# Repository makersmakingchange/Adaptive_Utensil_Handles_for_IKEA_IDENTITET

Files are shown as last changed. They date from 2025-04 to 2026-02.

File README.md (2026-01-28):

<!--- Open Source Assistive Technology: GitHub Readme Template Version 1.2 (2024-May-27)  --->

<!--- TITLE --->
# Adaptive Utensil Handles for IKEA IDENTITET

> [!IMPORTANT]
2026-Jan-28 The cutlery set is currently unavailable from IKEA Canada.

## Overview
<!--- A brief summary of the project. What it does, who it is for, how much it costs. --->
The Adaptive Utensil Handles for IKEA® IDENTITET™ is an assistive technology device that provides a cost-effective way for individuals who struggle to grasp and manipulate utensils to eat independently.

The handles are comprised of 3D printed parts that encapsulate the fork and/or spoon from the [commercially available IKEA® IDENTITET™ cutlery set](https://www.ikea.com/ca/en/p/identitet-16-piece-cutlery-set-stainless-steel-50578174/) . 

The Adaptive Utensil Handles are an open assistive technology (OpenAT). Under the terms of the open source licenses, the device may be built, used, and improved upon by anyone.

The overall cost of materials for a set of utensils and full set of handles is about $20 CAD.  

*IKEA® and IDENTITET™ are trademarks of Inter IKEA Systems B.V. This device is not affiliated with, endorsed by, or sponsored by IKEA.*

An IKEA Identitet fork in an adapted handle, along with several other handle variants.

## Makers Making Change Assistive Device Library
https://www.makersmakingchange.com/s/product/adaptive-utensil-handles-for-ikea-identitet/01tJR000008gxv7YAA 

## How to Obtain the Device
### 1. Do-it-Yourself (DIY) or Do-it-Together (DIT)

This is an open-source assistive technology, so anyone is free to build it. All of the files and instructions required to build the device are contained within this repository. Refer to the Maker Guide below.

### 2. Request a build of this device

You may also submit a build request through the [Makers Making Change Assistive Device Library Listing](https://www.makersmakingchange.com/s/product/adaptive-utensil-handles-for-ikea-identitet/01tJR000008gxv7YAA) to have a volunteer maker build the device. As the requestor, you are responsible for reimbursing the maker for the cost of materials and any shipping.

### 3. Build this device for someone else

If you have the skills and equipment to build this device, and would like to donate your time to create the device for someone who needs it, visit the [MMC Maker Wanted](https://makersmakingchange.com/maker-wanted/) section.

## Build Instructions
<!--- Outline the major steps required to create a build --->

### 1. Read through the Maker Guide

The [Maker Guide](/Documentation/Adaptive_Utensils_Maker_Guide.pdf)  contains all the necessary information to build this device, including tool lists, assembly instructions, programming instructions (if applicable) and testing.

### 2. Order the Off-The-Shelf Components

The [Bill of Materials](/Documentation/Adaptive_Utensils_BOM.xlsx) lists all of the parts and components required to build the device.

### 3. Print the 3D Printable components

All of the files and individual print files can be found in the [/Build_Files/3D_Printing_Files](/Build_Files/3D_Printing_Files/) folder.

### 4. Assemble the <DeviceName>

Reference the Assembly Guide section of the [Maker Guide](/Documentation/Adaptive_Utensils_Maker_Guide.pdf) for the tools and steps required to build the device.

## How to improve this Device
As open source assistive technology, you are welcomed and encouraged to improve upon the design. 

## Files
### Documentation
<!--- Update the name, link, and version for documentation --->
| Document             | Version | Link |
|----------------------|---------|------|
| Design Workbook     | 1.0     | [Adaptive_Utensils_Design_Workbook](/Documentation/Adaptive_Utensils_Design_Workbook.pdf)     |
| Design Rationale     | 1.0     | [Adaptive_Utensils_Design_Rationale](/Documentation/Adaptive_Utensils_Design_Rationale.pdf)     |
| Maker Guide          | 1.0     | [Adaptive_Utensils_Maker_Guide](/Documentation/Adaptive_Utensils_Maker_Guide.pdf)     |
| Bill of Materials    | 1.0     | [Adaptive_Utensils_Bill_of_Materials](/Documentation/Adaptive_Utensils_BOM.xlsx)     |
| User Guide           | 1.0     | [Adaptive_Utensils_User_Guide](/Documentation/Adaptive_Utensils_User_Guide.pdf)    |
| Changelog            | 1.0     | [Changelog](CHANGES.txt)     |

### Design Files
<!--- Include a copy of the original design files to facilitate easy editing and customization. Consider also including a generic format (e.g., STEP) --->
 - [CAD Files](/Design_Files/CAD_Design_Files)
 - [PCB Files](/Design_Files/PCB_Design_Files)

### Build Files
<!--- Include a copy of the build files intended for manufacturing. This may include svg files for laser cutting, stl files for 3d printing, Gerber files for custom PCBs, and Arduino files for custom firmware. --->
 - [3D Printing Files](/Build_Files/3D_Printing_Files)

## License
<!--- Add the year(s) for the copyright and the Designer Name. You may use the standard set of open licenses or choose your own for the hardware, software, and accompanying materials. --->
Copyright (C) 2024-2025, Alberta Health Services, Research and Innovation.

This work is licensed under a Creative Commons Attribution Non-commercial-Share Alike 4.0 International license. To view a copy of this licence, see https://creativecommons.org/licenses/by-nc-sa/4.0/. You are free to copy, distribute and adapt the work for non-commercial purposes, as long as you attribute the work to Alberta Health Services and abide by the other licence terms. If you alter, transform, or build upon this work, you may distribute the resulting work only under the same, similar, or compatible licence. The licence does not apply to AHS trademarks, logos or content for which Alberta Health Services is not the copyright 
owner.

This material is intended for general information only and is provided on an "as is", "where is" basis. Although reasonable efforts were made to confirm the accuracy of the information, Alberta Health Services does not make any representation or warranty, express, implied or statutory, as to the accuracy, reliability, completeness, applicability or fitness for a particular purpose of such information. This material is not a substitute for the advice of a qualified health professional. Alberta Health Services expressly disclaims all liability for the use of these materials, and for any claims, actions, demands or suits arising from such use.

## Attribution
<!--- Provide any necessary attribution for designs or components that are included in the device or as part of the project. --->
The device was designed and documented by Alberta Health Services, Research and Innovation. 

<!--- This is the attribution for the template. --->
The documentation template was created by Makers Making Change / Neil Squire Society and is used under a CC BY-SA 4.0 license. It is available at the following link: [https://github.com/makersmakingchange/OpenAT-Template](https://github.com/makersmakingchange/OpenAT-Template)

### Contributors
<!--- List the names of the people that contributed to the design. This could include the original source of the idea, designers, testers, documenters, etc. --->
 - Anson Chung 
 - Kendra Smart 
 - Holden Holzer
 - Tod Vandenberg
 - Michael Cimolini
 - Adam Bulat
 - Robert Hirsche

----

<!-- ABOUT MMC START -->
## About Makers Making Change
[Makers Making Change Logo](https://www.makersmakingchange.com/)

Makers Making Change is a program of [Neil Squire](https://www.neilsquire.ca/), a Canadian non-profit that uses technology, knowledge, and passion to empower people with disabilities.

Makers Making Change leverages the capacity of community based Makers, Disability Professionals and Volunteers to develop and deliver affordable Open Source Assistive Technologies.

 - Website: [www.MakersMakingChange.com](https://www.makersmakingchange.com/)
 - GitHub: [makersmakingchange](https://github.com/makersmakingchange)
 - Bluesky: [@makersmakingchange.bsky.social](https://bsky.app/profile/makersmakingchange.bsky.social)
 - Instagram: [@makersmakingchange](https://www.instagram.com/makersmakingchange)
 - Facebook: [makersmakechange](https://www.facebook.com/makersmakechange)
 - LinkedIn: [Neil Squire Society](https://www.linkedin.com/company/neil-squire-society/)
 - Thingiverse: [makersmakingchange](https://www.thingiverse.com/makersmakingchange/about)
 - Printables: [MakersMakingChange](https://www.printables.com/@MakersMakingChange)

### Contact Us
For technical questions, to get involved, or to share your experience we encourage you to [visit our website](https://www.makersmakingchange.com/) or [contact us](https://www.makersmakingchange.com/s/contact).
<!-- ABOUT MMC END -->

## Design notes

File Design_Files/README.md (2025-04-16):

<!--- Open Source Assistive Technology Template: GitHub Design Files Readme Version 1.2 (2025-Feb-04)  --->

This folder contains the design files for the device.

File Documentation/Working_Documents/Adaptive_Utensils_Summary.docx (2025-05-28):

# Overview

The Device Summary is intended to be a detailed summary of the device, product, and maker information for the Adaptive Utensils, making it easier to add to the Makers Making Change website. It is intended for anyone who will view the device listing.

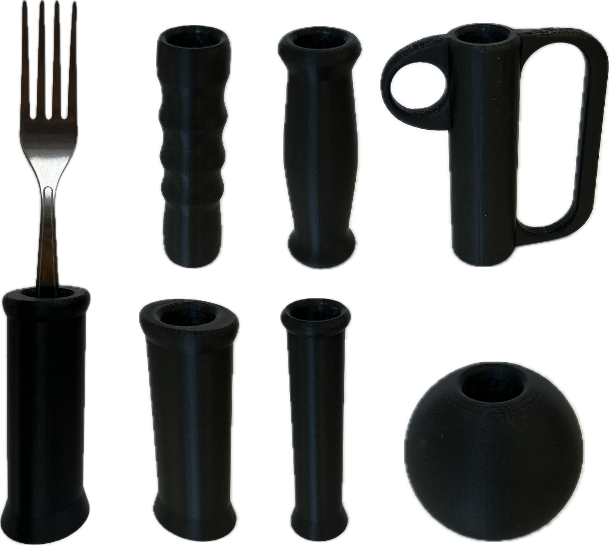
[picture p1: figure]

# Product Information

## Product Name

ADAPTIVE HANDLES FOR IKEA IDENTITET UTENSILS

## Device Category

Mark any relevant categories with an “X”:

| Adapted Toys
X | Aids for Daily Living (ADL)
| Assistive Switches
| Communication Aids (AAC)
| Computer Access
| Environmental Controls
| Gaming
| Keyguard
| Kits
| LipSyncs
| Mounting
| Recreation and Leisure
| Seating and Positioning
| Switch Interfaces
| Writing Aids

## User Value Statement

These 3D Printed Adaptive Utensils function as standard commercially available adaptive utensils in how they allow individuals with poor fine motor control to eat independently. Each of the handles offer a large, smooth area to grasp for improved ergonomics. Some handles mimic common shapes for commercial adaptive utensils, and others have more experimental shapes to explore the possibilities of 3D printing with adaptive utensils.

## Designer

Alberta Health Services, Research and Innovation

# Device Information

## Overview

This device acts as a cost effective substitution for commercial adaptive utensils which lowers the barrier-to-entry and allows individuals to trial different handle shapes to develop their own preference. Afterwards, users may 3D print more of their preferred handle or purchase a similar commercial adaptive utensil set for long-term usage.

## Disability Type

Select one or more disability types and mark with an “X”:

X | Agility / Dexterity
X | Arthritis
| Cognitive
| Hearing
| Mobility
| Pain
| SCI
| Vision
| Other

## Disability Type Description

The 3D printed Adaptive Utensils are for individuals who struggle to grasp and manipulate utensils. The affected patient population includes weakness in arm or grip strength, tremors/shakiness, limited range of motion, and poor fine motor skills.

## How To Use

Once assembled and properly adjusted, the 3D Printed Adaptive Utensils may be used as regular utensils to eat independently.

## Estimated Cost

The estimated material cost of the device for a single build:

| $0 - $10
X | $11 - $25
| $26 - $50
| $51 - $100
| $101 - $250
| $250+

## Attribution

Alberta Health Services, Research and Innovation

### Contributors

- Anson Chung
- Kendra Smart
- Holden Holzer
- Tod Vandenberg
- Michael Cimolini
- Adam Bulat
- Robert Hirsche

# Maker Information

## Project Skills

Mark the required project skills with an “X”:

X | 3D Printing
| Custom PCB
| Electronics
| Laser Cutting
| Mechanics
| Software
| Soldering
| Woodworking
| Other

## Skills Description

Requires basic 3D Printing skills for enabling support and slicing STL files.

## Tools Needed

X | 3D Printer
X | Common Hand Tools
| Common Power Tools
| Laser Cutter
| Soldering Iron
| Specialized Tooling

## Print time (hrs)

17.5 hours

## Assembly time (hrs)

0.25 hours

## Build Instructions

Requires approximately 22 g of PETg and 330 g of PLA 3D printing filament as well as 1 large spoon and 1 large fork from the IKEA IDENTITET utensil set.

Auto-orient and enable supports for each STL, then 3D print all required parts. When complete, assemble the core assembly around each utensil and test the fits inside each handle.

## Download Link

https://github.com/makersmakingchange/Adaptive_Utensil_Handles_for_IKEA_IDENTITET/archive/refs/heads/main.zip

## Project Link

# https://github.com/makersmakingchange/Adaptive_Utensil_Handles_for_IKEA_IDENTITET

# License

## License

CC BY SA 4.0 License

© 2024-2025 by Alberta Health Services, Research and Innovation This work is licensed under the CC BY SA 4.0 License: http://creativecommons.org/licenses/by-sa/4.0 Files available at https://github.com/makersmakingchange/Adaptive_Utensil_Handles_for_IKEA_IDENTITET Page 1 of 2

V2.0.0 | January 2025 Adaptive Utensil Handles for IKEA IDEN Summary

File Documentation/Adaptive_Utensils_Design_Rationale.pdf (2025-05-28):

V2.0.0 | January 2025

## Adaptive Utensils

## DESIGN RATIONALE

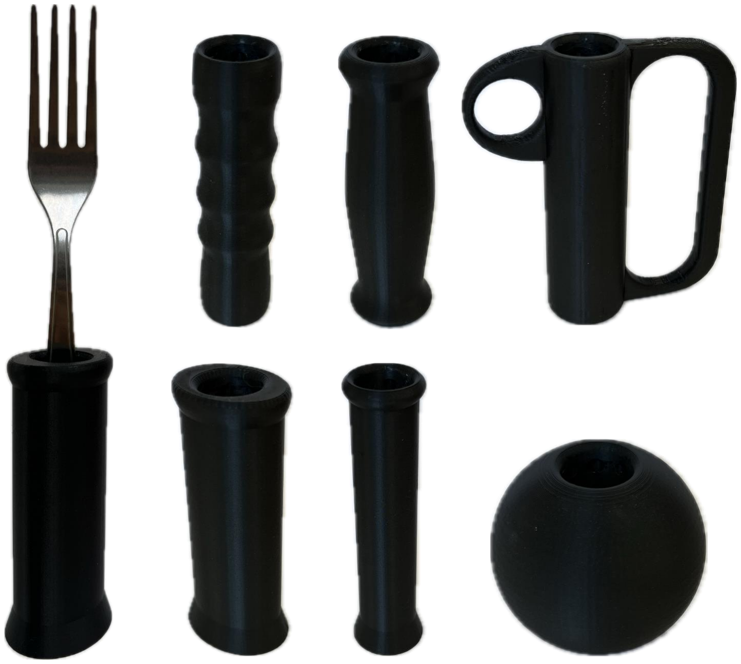
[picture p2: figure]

© 2024 by Alberta Health Services, Research and Innovation This work is licensed under the CC BY SA 4.0 License: http://creativecommons.org/licenses/by-sa/4.0
Files available at https://github.com/makersmakingchange/Adaptive_Utensil_Handles_for_IKEA_IDENTITET | Page 1 of 24

### Overview

The Design Rationale is intended to provide designers and maker information about the design process and design decisions behind the development of the Adaptive Utensils, a set of adjustable and interchangeable 3D printed adaptive utensil handles.

## DESIGN RATIONALE

Files available at https://github.com/makersmakingchange/Adaptive_Utensil_Handles_for_IKEA_IDENTITET | Page 2 of 24

### Contents

Overview | 1
Introduction | 4
Requirements | 4
Goals | 4
Functional Requirements | 4
Non-functional Requirement | 4
Constraints | 5
Research | 6
Commercially Available Options | 6
Special Supplies Adaptive Utensils | 6
Vincere Silverware Weighted Utensils | 7
Special Supplies Bendable Adaptive Utensils | 8
DIY / Maker-Friendly Options | 8
Fork and Spoon Support | 8
Universal hand grip for cutlery | 9
Ideation | 10
Ideation Decisions | 11
Conceptual Designs | 11
Core Mechanism (ID03) | 11
Physical Component / Enclosure | 12
Concept Decisions | 13
Prototyping | 14
GRH 2-Part Core (AU Rev01) | 14
Physical Component / Enclosure | 14
IKEA Hinged Core (AU Rev02) | 15
Physical Component / Enclosure | 15
Prototype Decisions | 16
Testing | 17
Test Methods | 17
GRH 2-Part Core First Demo (TEST 1.1) | 17

## DESIGN RATIONALE

Files available at https://github.com/makersmakingchange/Adaptive_Utensil_Handles_for_IKEA_IDENTITET | Page 3 of 24
IKEA 2-Part Core First Demo (TEST 2.1) | 17
IKEA 2-Part Core Second Demo (TEST 2.2) | 17
IKEA 2-Part Core Third Demo (TEST 2.3) | 17
Test Results | 17
Detailed Design | 19
Physical Component / Enclosure | 19
Opportunities for Improvement | 24
Physical Component / Enclosure | 24

## DESIGN RATIONALE

Files available at https://github.com/makersmakingchange/Adaptive_Utensil_Handles_for_IKEA_IDENTITET | Page 4 of 24

### Introduction

Commercially available adaptive utensils are expensive commitments where buyers are unable to trial different styles of handles and determine what best suits their needs. Some purchased sets cannot be returned, which may leave individuals with adaptive utensils that are uncomfortable to use.

The 3D printed Adaptive Utensils play the same role as commercially available adaptive utensils, which is to allow individuals with poor fine motor control to eat independently. However, the 3D printed handles fulfill a different niche in how they are fast and cheap to manufacture, which lowers the barrier-to-entry and lets individuals trial different handle shapes to develop their own preference. Afterwards, users may 3D print more of their preferred handle or purchase a similar commercial adaptive utensil set for long-term usage.

The 3D printed Adaptive Utensils are for individuals who struggle to grasp and manipulate utensils. The affected patient population includes weakness in arm or grip strength, tremors/shakiness, limited range of motion, and poor fine motor skills.

### Requirements

The goals and requirements outlined here can be used to assess if a device would meet the needs of a user and determine when a design is sufficient for release.

### Goals

G01 | Handles must be significantly larger than a typical utensil handle and feel ergonomic to hold to reduce the strain on fingers
G02 | Must be compatible with at least a spoon and fork.
G03 | There should be as few components as possible to reduce the risk of misplacing them
G04 | Handles should be simple and quick to order/manufacture

### Functional Requirements

F01 | Utensil must be interchangeable with different types of handles
F02 | Adjustable depth for utensil in handle
F03 | Adjustable rotation for utensil in handle
F04 | Utensil must lock in place during regular usage

### Non-functional Requirement

NF01 | Create smooth geometry where possible to improve the overall appearance and feel of the printed handles
NF02 | Imitate common shapes for commercial adaptive utensils so users can test those styles before buying them

## DESIGN RATIONALE

Files available at https://github.com/makersmakingchange/Adaptive_Utensil_Handles_for_IKEA_IDENTITET | Page 5 of 24

### Constraints

C01 | Printed handle sets must be cheaper than generic commercial adaptive utensils (maximum $30 CAD per set)
C02 | Use PLA and/or PETG, as they are the most common 3D printing materials

## DESIGN RATIONALE

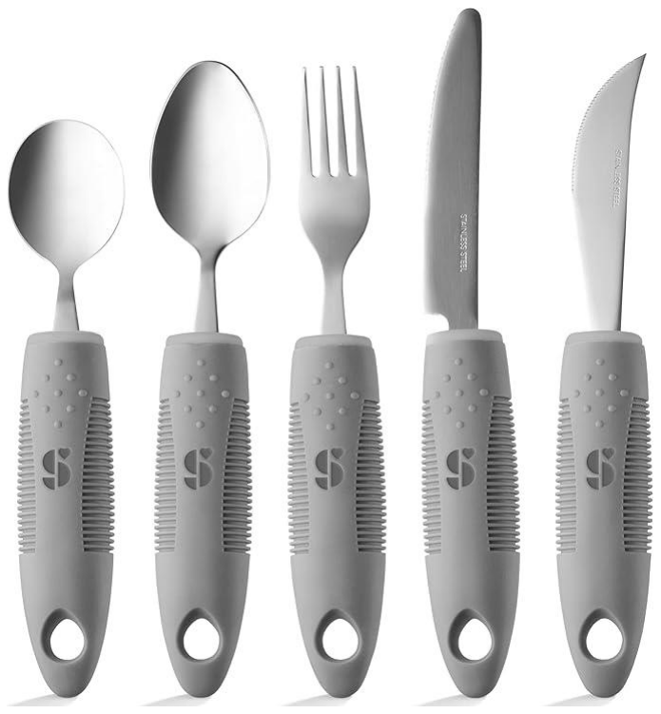
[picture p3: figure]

Files available at https://github.com/makersmakingchange/Adaptive_Utensil_Handles_for_IKEA_IDENTITET | Page 6 of 24

### Research

In 2022, two occupational therapists (OTs) at the Glenrose Rehabilitation Hospital brought up a problem to the Research and Innovation department about patients being unable to test different types of adaptive utensils before committing to buying them. In the current state, most patients have no experience or preference with adaptive utensils, and therapists have little information to determine if an adaptive utensil would help and which type would be the best option for their patient.

Thus, to allow patients to test various adaptive utensils for themselves, a project was started to develop cheap 3D printed Adaptive Utensils. The 3D printed handles should act as commercial adaptive utensils but should be cheap to manufacture and primarily act as a trial option before opting to buy a commercial set. To help the testing process, the handles should be compatible with a standard type of utensils, which should be quick to swap and adjust within each handle.

### Commercially Available Options

Options that can be purchased but not made by a maker.

Special Supplies Adaptive Utensils
Title / Name of device | Special Supplies Adaptive Utensils (4-Piece Kitchen Set) Wide Non-Weighted Non-Slip Handles for Hand Tremors Arthritis Parkinson's or Elderly use | Stainless Steel Knife Fork Spoons - Grey
Link | Amazon Link (https://www.amazon.ca/Adaptive-Utensils-Non-Weighted-Arthritis-Parkinsons/dp/B074JH1T1N?rnid=11192166011&s=hpc)
Author | Brand: Special Supplies. Distributor: Amazon
License | N/A
Cost | $35.00 CAD

## DESIGN RATIONALE

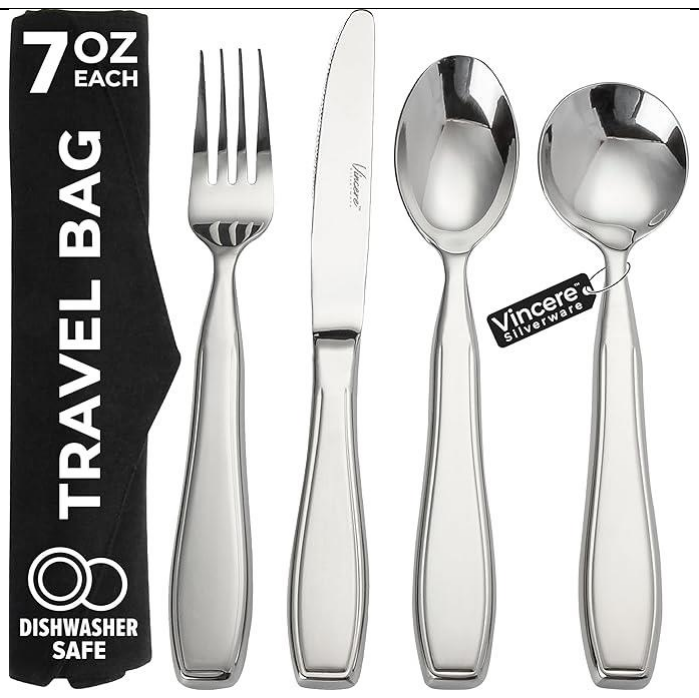
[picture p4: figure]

Files available at https://github.com/makersmakingchange/Adaptive_Utensil_Handles_for_IKEA_IDENTITET | Page 7 of 24

Non-weighted adaptive utensils that are dishwasher safe, have stainless-steel utensils, and ribbed silicone handles for improved grip. Each set includes a fork, knife, curved knife, dinner spoon, and soup spoon.

Requirements Met | Requirements Unmet
G01, G02, G03, G04, F04, NF01 | F01, F02, F03, NF02

Useful Design Features
Utensils are dishwasher safe, which makes cleaning quick and easy.

Vincere Silverware Weighted Utensils
Title / Name of device | Weighted Utensils for Tremors and Parkinsons, Heavy Weight Stainless Steel Silverware Set, Adaptive Eating Flatware Helps Hand Tremors, Parkinsons Aids for Living, Arthritis - Knife, Fork, Spoons, 7oz
Link | Amazon Link (https://www.amazon.ca/Weighted-Utensils-Tremors-Parkinsons-Silverware/dp/B07YNSJDW6?rnid=11192166011&s=hpc)
Author | Brand: Vincere Silverware. Distributor: Amazon
License | N/A
Cost | $99.95 CAD

7oz weighted utensils designed to improve stability for individuals with tremors. They are dishwasher safe, but do not have a significantly larger handle like typical adaptive utensils. Each set includes a knife, fork, tablespoon, and soup spoon.

Requirements Met | Requirements Unmet
G02, G03, G04, F04, NF01 | G01, F01, F02, F03, NF02

Useful Design Features
The weighted design should help reduce shaky hands from tremors.

## DESIGN RATIONALE

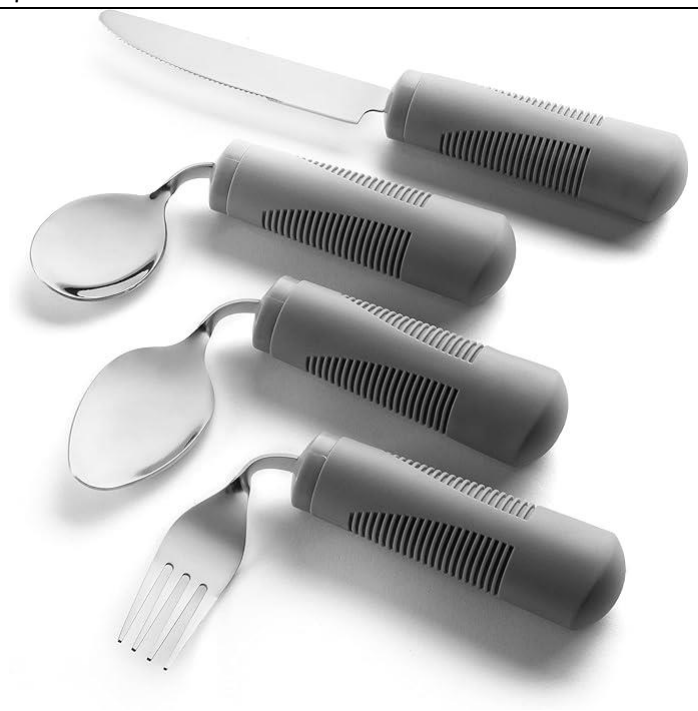
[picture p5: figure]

Files available at https://github.com/makersmakingchange/Adaptive_Utensil_Handles_for_IKEA_IDENTITET | Page 8 of 24

Special Supplies Bendable Adaptive Utensils
Title / Name of device | Special Supplies Adaptive Utensils (4-Piece Kitchen Set) Wide Weighted Non-Slip Handles for Hand Tremors Arthritis Parkinson‚ or Elderly use | Stainless Steel Knife Fork Spoons (Gray Weighted Bendable)
Link | Amazon Link (https://www.amazon.ca/Adaptive-Utensils-Weighted-Arthritis-Parkinsons/dp/B07JCF9HW3?rnid=11192166011&s=hpc)
Author | Brand: Special Supplies. Distributor: Amazon
License | N/A
Cost | $33.40 CAD

6oz weighted adaptive utensils that are dishwasher safe, have bendable stainless-steel utensils, and ribbed silicone handles for improved grip. Each set includes a fork, knife, dinner spoon, and soup spoon.

Requirements Met | Requirements Unmet
G01, G02, G03, G04, F03, F04, NF01 | F01, F02, NF02

Useful Design Features
Utensils are bendable for more user customizability.

### DIY / Maker-Friendly Options

Options that can be made by a maker.

Fork and Spoon Support
Title | Fork and Spoon Support
Link | Makers Making Change Link (https://www.makersmakingchange.com/s/product/fork-and-spoon-support/01tJR00000068zYYAQ)
Author | MMC Community
License | Attribution-NonCommercial-ShareAlike4.0 International
Cost | $0-$10 CAD
Test Build (Y/N) | N
Add to Library (Y/N) | Already Added

## DESIGN RATIONALE

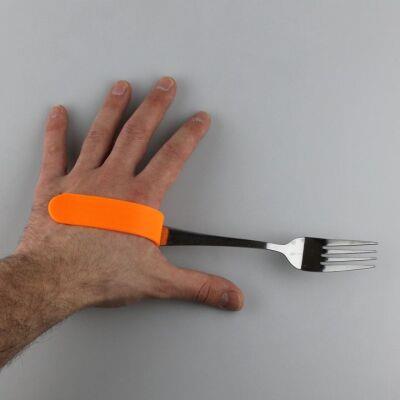
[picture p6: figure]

Files available at https://github.com/makersmakingchange/Adaptive_Utensil_Handles_for_IKEA_IDENTITET | Page 9 of 24

The Fork and Spoon Support allows people with limited grip strength to hold and use eating utensils. Users can slot the device over their palm for a grip-free usage or hold both handles for a larger grip. The slot fits standard sized eating utensils like forks, spoons, and knives.

Requirements Met | Requirements Unmet
G01, G02, G03, G04, F02, F04, NF01 | F01, F03, NF02

Useful Design Features
Compatible with a wide variety of utensils. Clips around the hand and does not require individuals to grip anything.

Universal hand grip for cutlery
Title | Universal hand grip for cutlery
Link | Thingiverse Link (https://www.thingiverse.com/thing:686084)
Author | Pole_ergo
License | Creative Commons – Attribution – Non-commercial 4.0 International
Cost | $0-$10 CAD
Test Build (Y/N) | N
Add to Library (Y/N) | N

## DESIGN RATIONALE

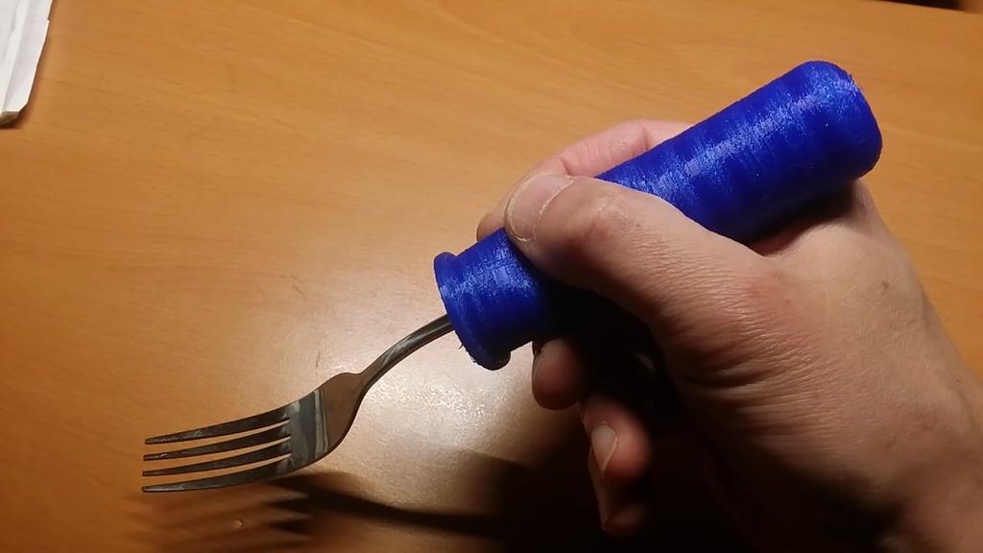
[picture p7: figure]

Files available at https://github.com/makersmakingchange/Adaptive_Utensil_Handles_for_IKEA_IDENTITET | Page 10 of 24

3D printed handle for flat metal fork/spoon/knife. Must be printed in a soft material like Ninjaflex, where infill density will affect the overall rigidity of the handle.

Requirements Met | Requirements Unmet
G01, G02, G03, G04, F02, F04, NF01 | F01, F03, NF02

Useful Design Features
Soft material makes the handle compatible with a wide variety of utensil handles and makes the outer shell conform to the user’s grip.

### Ideation

Epoxy Assembly (ID01): 3D print 2 halves of each adaptive handle with a slot cut out to fit the utensil. Insert the utensil between handle halves and use epoxy to affix all 3 parts together.

Friction Fit (ID02): Slide utensil into a 3D printed handle and lock in place with a friction fit. Similar idea as the DIY option above (Universal hand grip for cutlery).

## DESIGN RATIONALE

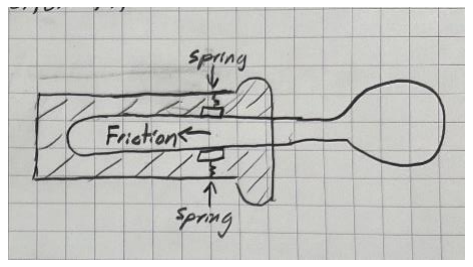
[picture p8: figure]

Files available at https://github.com/makersmakingchange/Adaptive_Utensil_Handles_for_IKEA_IDENTITET | Page 11 of 24

Core Mechanism (ID03): 3D print core mechanism to clamp around the utensil, where the core can be inserted and locked into different 3D printed handles

### Ideation Decisions

Idea | Decision (Abandon, Modify, Proceed) | Justification
Epoxy Assembly (ID01) | Abandon | Requires a utensil and significant assembly time for each handle that is made. Epoxy is permanent, which means the utensil cannot be removed and placed in a dishwasher.
Friction Fit (ID02) | Abandon | Does not offer much adjustability. Friction force is unreliable because the 3D prints will wear over time.
Core Mechanism (ID03) | Proceed | Clamping around a utensil handle will require some friction, but because the core will be a smaller part, it will be easier to replace if it wears down. A clamp is a non-permanent option so the utensil may be removed and placed in a dishwasher. The core assembly should be able to be inserted into each of the 3D printed handles while offering some adjustability and locking mechanism.

### Conceptual Designs

### Core Mechanism (ID03)

Core mechanism to clamp around utensil and swap between 3D printed adaptive handles

## DESIGN RATIONALE

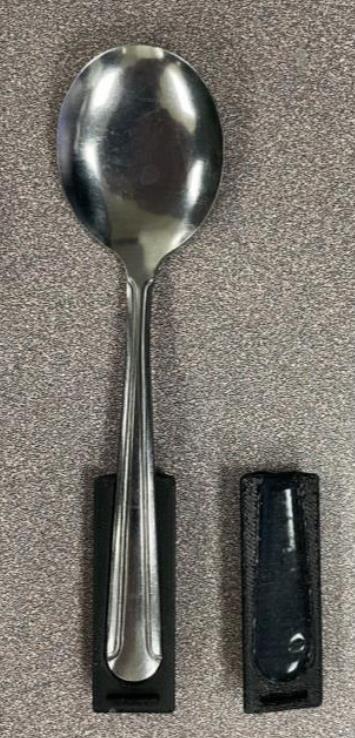
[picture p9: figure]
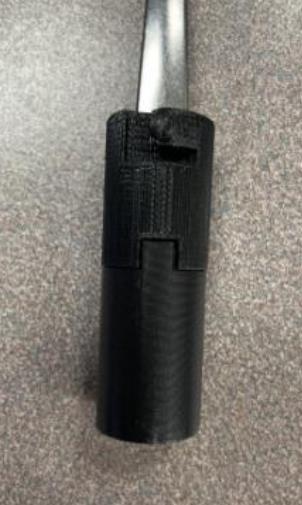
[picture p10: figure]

Files available at https://github.com/makersmakingchange/Adaptive_Utensil_Handles_for_IKEA_IDENTITET | Page 12 of 24

Physical Component / Enclosure
The utensils used for the initial concept were the standard Glenrose Rehabilitation Hospital cutlery because the original focus was for inpatients.

Because the base of the utensil handle is large and it tapers inwards moving towards the “eating end”, the utensil can be held by cutting a profile of the utensil into the core and clamping it shut. We created a clamping mechanism using two halves of a cylinder and a collar/shell that slides around everything to keep the core closed. To lock positioning, the core will have a compliant mechanism with a ball socket and the handles have corresponding hemisphere cutouts inside at various depths and rotations. When inserting the core into a handle, the ball is pressed inwards and is continuously exerting force to spring back outwards. When the ball socket is aligned with a hemisphere cutout, then the ball pushes out and locks the core assembly inside the handle.

## DESIGN RATIONALE

Files available at https://github.com/makersmakingchange/Adaptive_Utensil_Handles_for_IKEA_IDENTITET | Page 13 of 24

### Concept Decisions

Concept | Decision (Abandon, Modify, Proceed) | Justification
Core Mechanism (ID03) | Proceed | The core was promising because it was the only idea that could non-permanently hold the utensil without significant risk of wear over time. It also has the best potential for being: insertable, removable, have depth adjustment, have rotation adjustment, and be able to lock in position. Only having to swap the core between handles means that fewer utensils and less assembly time would be required to test out various types of handles.

## DESIGN RATIONALE

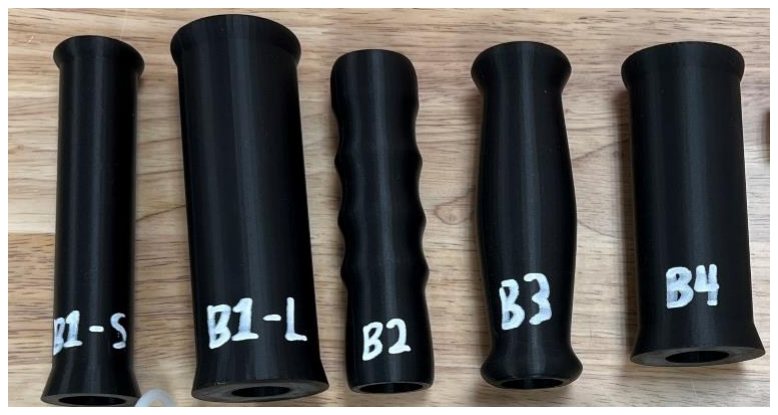
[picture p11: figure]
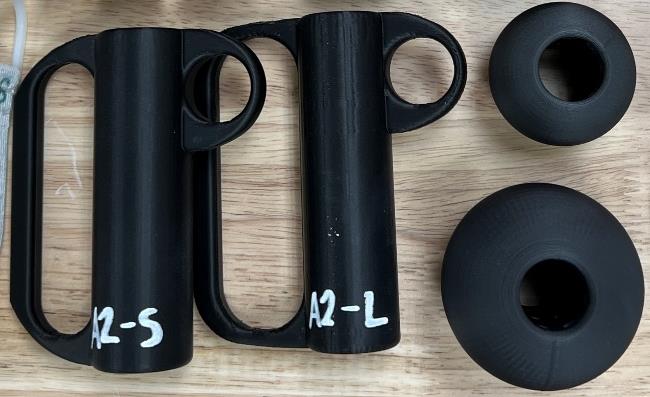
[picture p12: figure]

Files available at https://github.com/makersmakingchange/Adaptive_Utensil_Handles_for_IKEA_IDENTITET | Page 14 of 24

### Prototyping

### GRH 2-Part Core (AU Rev01)

2-part adaptive utensil cores designed for the standard Glenrose Rehabilitation Hospital cutlery.

Physical Component / Enclosure
The utensils used for the first prototype (AU Rev01) were the standard Glenrose Rehabilitation Hospital cutlery because the original focus was for inpatients.

The 2-part cores are 2 halves of a cylinder with a tapered slot cut out to fit the base of the utensil and prevent it from sliding upwards out of the core. The cylinder is held shut by sliding a 3D printed shell around the cylinder halves.

We quickly realized that the core cutouts need to match as perfectly as possible with the utensil bases or else they would have too much wiggle room and fall out of the core. So, to produce a minimum viable product (MVP), we decided to reduce the development time by limiting the utensil options to a large spoon and fork.

As per the Core Mechanism idea (ID03), we made a compliant mechanism to lock the core into any of the 3D printed handles. Inside the handles, there are 3 rings of 8 hemisphere cutouts, for a total of 24 cutouts. When the core is inserted into a handle, the compliant mechanisms push outwards and lock in place when aligned with the hemisphere cutouts. This allows for 3 levels of depth adjustment in increments of 20mm and for 8 levels of rotation adjustment in increments of 45°.

There were 9 handles designed for this project: Straight-Small, Straight-Large, Finger Grip, Rounded Grip, Ellipse, Finger Support-Small, Finger Support-Large, Sphere-Small, and Sphere-Large. More details on the handle shapes, styles, and sizes can be found in the Detailed Design section.

The cores are printed out of PETG for more abrasion resistance and tolerance consistency. The handles are printed out of PLA for cost effectiveness and ease of manufacturing.

## DESIGN RATIONALE

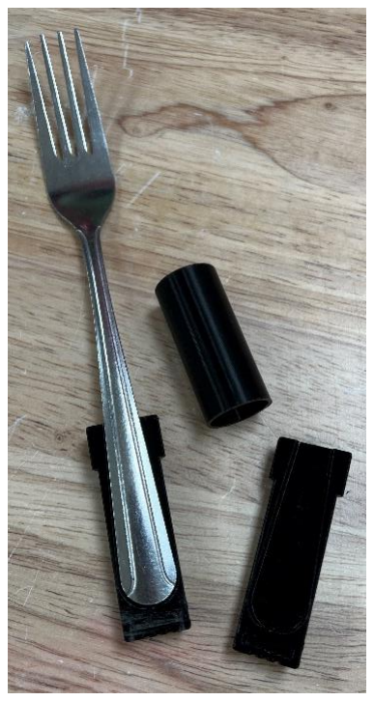
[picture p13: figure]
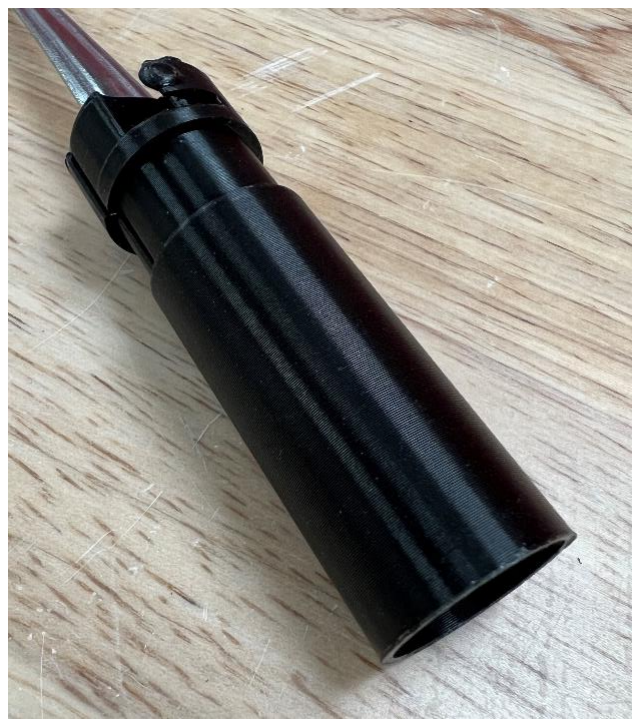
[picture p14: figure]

Files available at https://github.com/makersmakingchange/Adaptive_Utensil_Handles_for_IKEA_IDENTITET | Page 15 of 24

### IKEA Hinged Core (AU Rev02)

Adaptive utensil cores with a print-in-place hinge designed for the IKEA IDENTITET cutlery set.

Physical Component / Enclosure
The utensils used for the second prototype (AU Rev02) were the IKEA IDENTITET cutlery because the focus has been shifted to public accessibility.

The core cylinder halves have been combined into one part by taking advantage of a print-in-place hinge. And to improve the core’s locking strength in the handle, a second ball socket was added on the opposite side of the core. The tapered slot cutout was adapted to the IKEA IDENTITET large spoon and fork, and in doing so, the 3D printed handles had to be upscaled to fit the larger cores for the new utensil profiles.

The hemisphere cutouts, handle types, and material choices remain unchanged from AU Rev01.

## DESIGN RATIONALE

Files available at https://github.com/makersmakingchange/Adaptive_Utensil_Handles_for_IKEA_IDENTITET | Page 16 of 24

### Prototype Decisions

Prototype Decision (Abandon, Modify, Proceed)

Justification

GRH 2-Part Core
(AU Rev01)
Modify | The standard GRH utensils would be good for hospital use,
but they are not accessible to the general public. In addition, the utensils were thin, which made it difficult to achieve a strong grip on them with the cores.
The cylinder halves that make up the core function as intended, but they add extra components that may be misplaced. The next prototype should try to consolidate the two parts into one using hardware, snap fits, living hinges, etc.
The locking sockets worked well, but the ball tips showed significant wear over time. To make a better hold, there should be a second ball socket placed opposite to the original one. This will double the locking strength and improve the core’s stability inside the handles.

IKEA Hinged Core
(AU Rev02)
Proceed | Changing to IKEA IDENTITET utensils improves both
accessibility and functionality. IKEA has nearly 500 stores worldwide and has a reputation of consistency to allow more makers to acquire the exact utensil set used for this build. Additionally, the IDENTITET utensil handles are wider and have a steeper taper (in comparison to the GRH utensils), which makes it easier for the core to grip the utensil base.
The cylinder halves are now combined to print as one part using a print-in-place hinge, which improves the overall ease of use.
There are now 2 locking sockets in the core mechanism. This improves the stability by adding another point of contact as well as increases the lifespan of the part by strengthening the lock.

## DESIGN RATIONALE

Files available at https://github.com/makersmakingchange/Adaptive_Utensil_Handles_for_IKEA_IDENTITET | Page 17 of 24

### Testing

### Test Methods

The 3D printed Adaptive Utensils were only tested for useability by occupational therapists and patients, which is not repeatable. Each test below describes different periods of user testing and the resultant feedback to improve the device.

GRH 2-Part Core First Demo (TEST 1.1)
The first prototypes (AU Rev01) of the 3D printed Adaptive Utensils were given to 2 occupational therapists for testing. This version was designed for the standard GRH cutlery, and the defining features were the 2-part half-cylinder cores.

After some testing, it was clear that the GRH utensils did not suit the use-case for this device. The utensils occasionally slipped out of the core due to their thin profile, which left the core stuck inside the handles. With the cores’ slot cutouts being dedicated to a specific utensil handle, it was a slight hinderance to find the matching cylinder halves for assembly.

IKEA 2-Part Core First Demo (TEST 2.1)
The second prototypes (AU Rev02) were given to the same OTs for testing. This version was designed for the IKEA IDENTITET utensils and hosted the single-piece cores with print-in-place hinges.

With a new size, the tolerance between the cores and handles changed such that: the fits between certain handles varied slightly; the core shells occasionally got stuck inside certain handles when removing the core; and the cores did not lock within the handles during regular usage of the utensils.

IKEA 2-Part Core Second Demo (TEST 2.2)
AU Rev02 was modified and underwent the same testing conditions. This version had improved tolerances and an improved core locking strength.

The changes drastically improved the consistency and ease of use. The next issue was that, since the handles have the same diameter hole cut through the whole length, some users may try to insert the cores in the wrong side of the handle.

IKEA 2-Part Core Third Demo (TEST 2.3)
AU Rev02 was modified again and underwent the same testing conditions. This version had slightly closed off the bottom holes of each handle such that the core could not be inserted the wrong way.

In this testing session, the occupational therapists liked the new design and had no more suggestions for improvement.

### Test Results

For TEST 1.1, the primary critiques regarded the core assembly. The cores were unable to firmly hold the utensil bases due to the thin profile of the utensils. The separate cylinder halves added more time to organization and assembly. From TEST 1.1, the utensils were changed to the IKEA IDENTITET set for a

## DESIGN RATIONALE

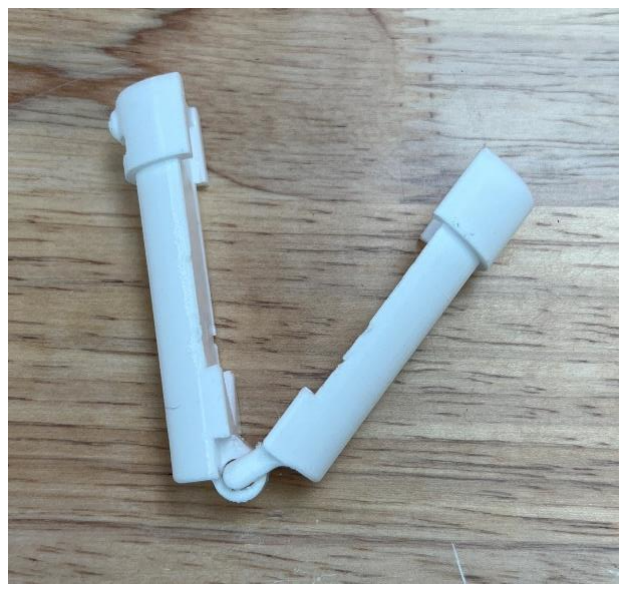
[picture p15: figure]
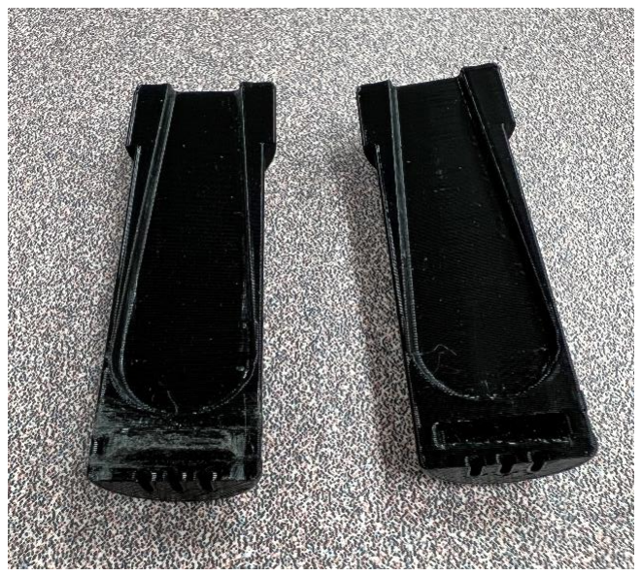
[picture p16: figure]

Files available at https://github.com/makersmakingchange/Adaptive_Utensil_Handles_for_IKEA_IDENTITET | Page 18 of 24

thicker profile as well as for more accessibility outside of the hospital. Additionally, there was a print-in-place hinge added to the core such that each fork/spoon core prints as one piece and cannot be separated or mismatched.

For TEST 2.1, the primary critiques regarded the tolerance. The fits were not uniform, and the core assemblies did not lock while still being easily removable. The handle models for AU Rev02 were tweaked to create a more universal fit with the core, and in doing so, the core shells no longer got stuck inside the handles. Then to create a stronger hold for the cores, a second ball socket was added to the opposite side to double the force pushing outwards in the hemisphere cutouts.

TEST 2.2 had positive feedback for all previous changes. The only issue from this testing period was about potential for misuse by inserting cores into the wrong side of the handles. Using the wrong side means that the locking mechanism would not work because the hemisphere cutout layers are positioned near the tops of each handle. To prevent this, the bottoms of each handle were slightly closed off such that the cores would not fit but were still open for cleaning access.

## DESIGN RATIONALE

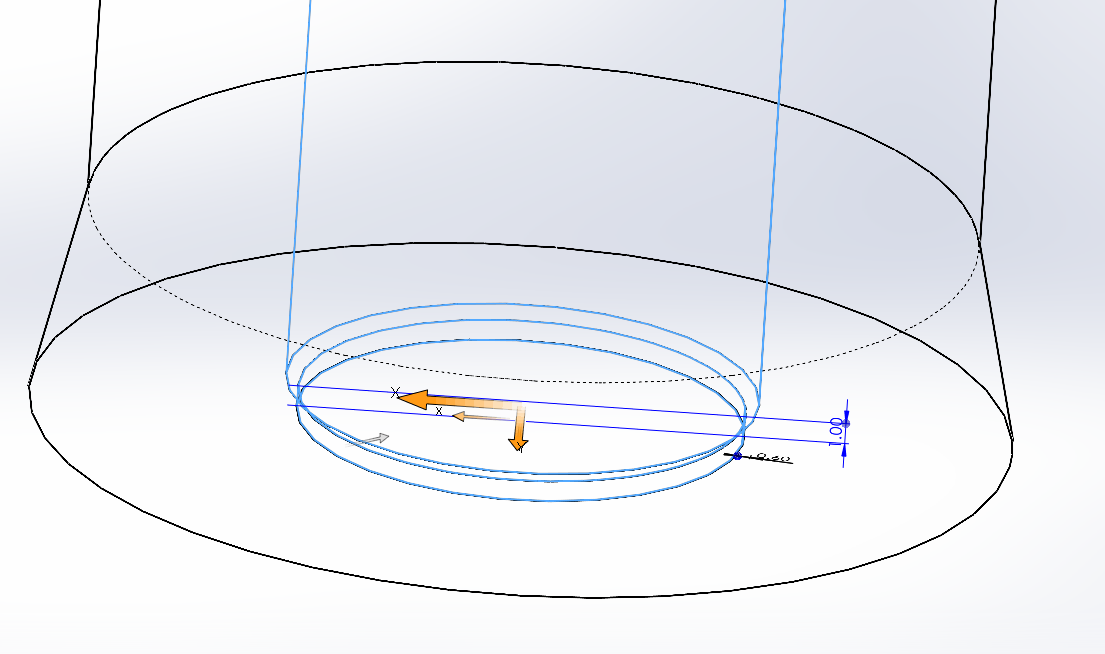
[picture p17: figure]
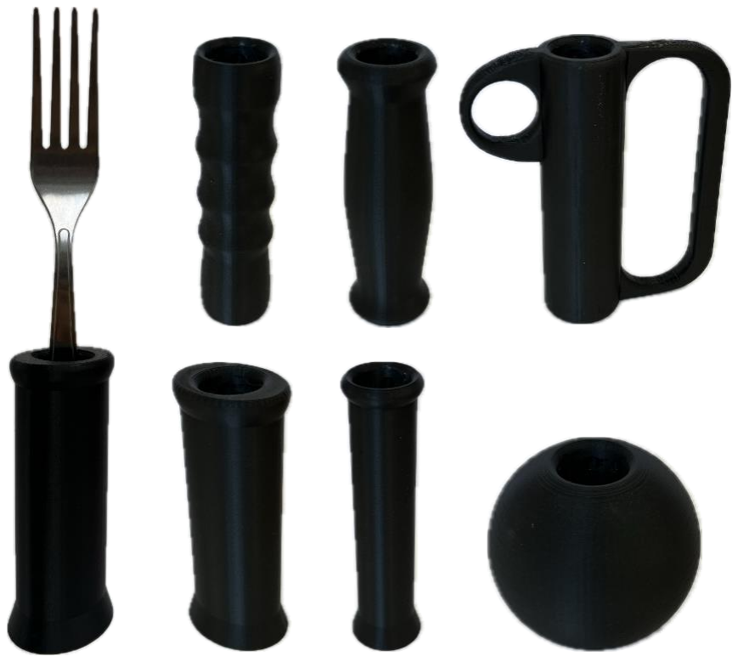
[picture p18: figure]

Files available at https://github.com/makersmakingchange/Adaptive_Utensil_Handles_for_IKEA_IDENTITET | Page 19 of 24

TEST 2.3 had positive feedback again. The OTs did not have any more feedback and stated that the project is ready for completion.

### Detailed Design

The 3D printed Adaptive Utensils consist of core assemblies to hold the IKEA IDENTITET utensils and various handles to lock the utensil cores in place at different depths and rotations.

Physical Component / Enclosure
The cores have 2 separate models with specific slot cutouts to hold the IKEA IDENTITET large spoon and fork profiles (G02). Separate colors help differentiate the core profiles, so the spoon core is commonly

## DESIGN RATIONALE

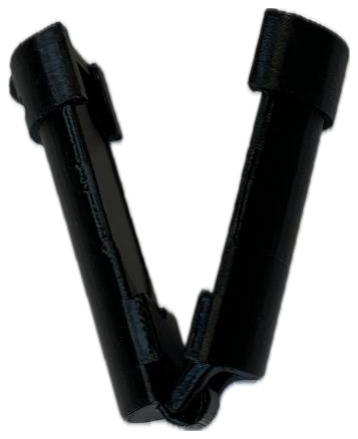
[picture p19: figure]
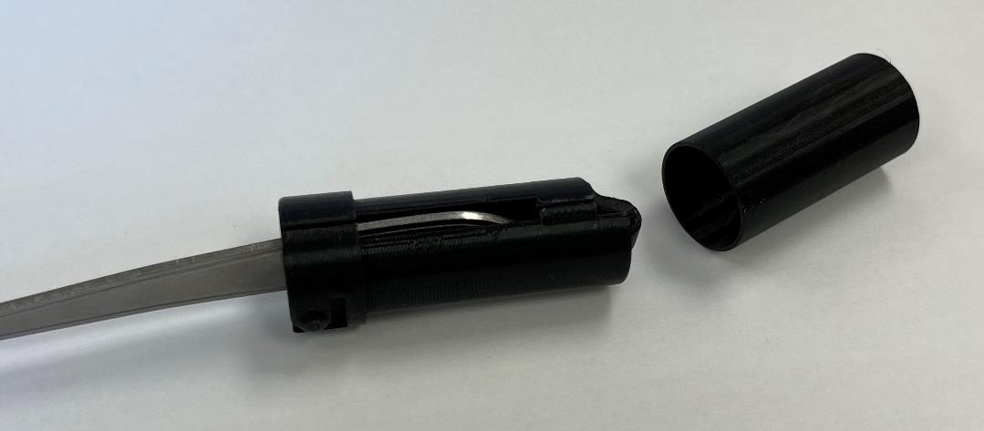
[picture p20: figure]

Files available at https://github.com/makersmakingchange/Adaptive_Utensil_Handles_for_IKEA_IDENTITET | Page 20 of 24

printed with white PETG and the fork core is commonly printed with black PETG. Otherwise, the core types can be labeled with a permanent marker.

The core is designed to clamp around the utensil bases, where a separate shell slides around the core clamp to lock it closed. The 2 cylinder halves of the core clamp are designed with a print-in-place hinge to print as one part, which reduces assembly time as well as risk of misplacing pieces (G03). Both fork and spoon cores have a universal fit such that they are interchangeable between all of the 3D printed handles (F01).

## DESIGN RATIONALE

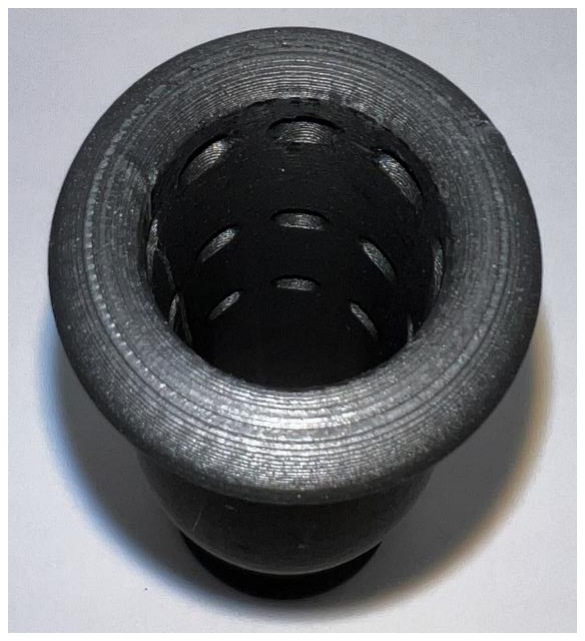
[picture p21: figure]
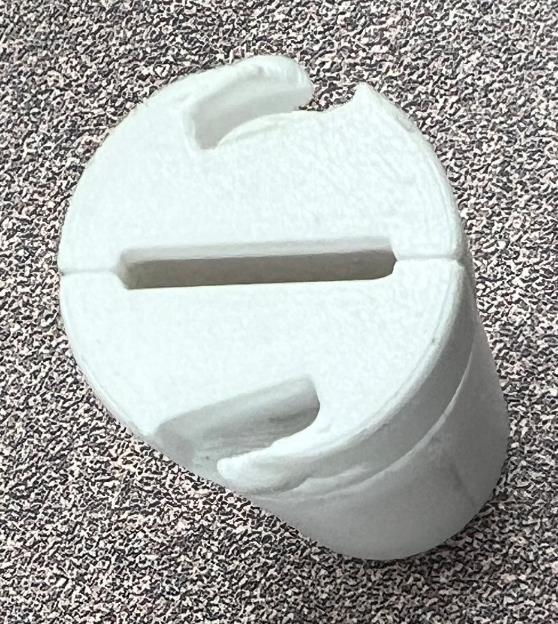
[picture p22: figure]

Files available at https://github.com/makersmakingchange/Adaptive_Utensil_Handles_for_IKEA_IDENTITET | Page 21 of 24

The core clamps have two locking ball sockets with compliant spring mechanisms to push outwards when inserted into the handles. There are 24 hemisphere cutouts inside each handle that allow the ball sockets to push outwards into the corresponding cavities, thus locking the core in place within the handle (F04). The cutouts are arranged in 3 rings of 8, which allow for 3 levels of depth adjustment in increments of 20mm (F02) and for 8 levels of rotation adjustment in increments of 45° (F03).

## DESIGN RATIONALE

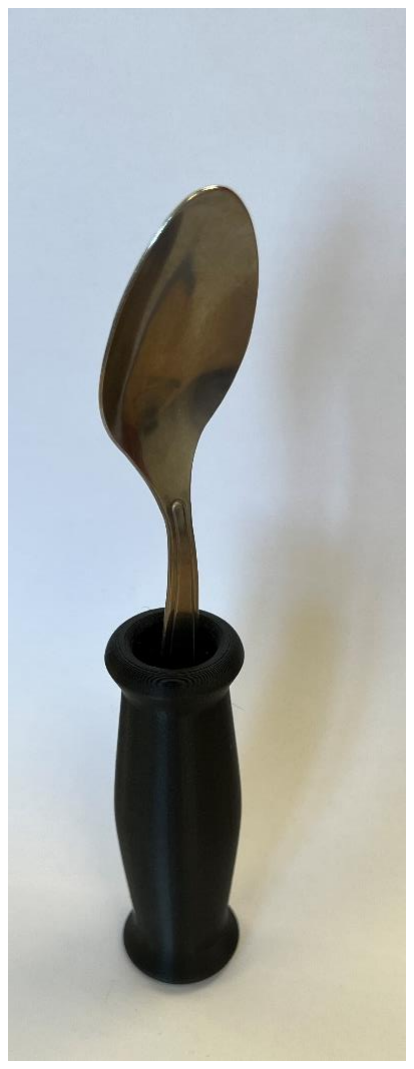
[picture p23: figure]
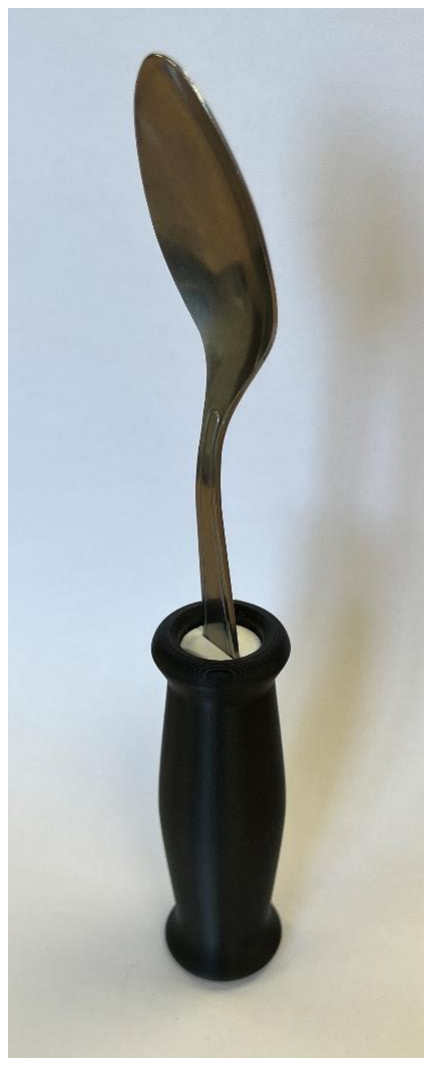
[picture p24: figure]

Files available at https://github.com/makersmakingchange/Adaptive_Utensil_Handles_for_IKEA_IDENTITET | Page 22 of 24

Each of the handles are printed with PLA filament, where they offer a larger area to grasp and feel ergonomic to hold (G01) due to their smooth geometry (NF01). Some handles mimic common shapes for commercial adaptive utensils (NF02), and others have more experimental shapes to explore the possibilities of 3D printing with adaptive utensils. The parts are easy to print due to the simple designs (G04). They are more accessible than commercially available adaptive utensils because they are 3D printable with common materials such as PLA and PETG (C02) and they are cheap (C01) due to a low upfront manufacturing cost.

There are 9 different types of handles for the 3D printed Adaptive Utensils:

- Ellipse
- Cylinder handle with an oval cross section shape.
- Finger Grip
- Handle with finger groove indentations.
- Finger Support-Large
- Has rigid support around the fingers and thumb. The larger version has a 33mm spacing for the finger support.
- Finger Support-Small

## DESIGN RATIONALE

Files available at https://github.com/makersmakingchange/Adaptive_Utensil_Handles_for_IKEA_IDENTITET | Page 23 of 24
- Has rigid support around the fingers and thumb. The smaller version has a 27mm spacing for the finger support.
- Rounded Grip
- Rounded handle that is thickest in the middle and tapers thinner at the top and bottom.
- Sphere-Large
- Spherical handle. The larger version has a 70 mm diameter sphere.
- Sphere-Small
- Spherical handle. The smaller version has a 52 mm diameter sphere.
- Straight-Large
- Cylinder handle with a circular cross section. The larger version has a 42 mm diameter cross section.
- Straight-Small
- Cylinder handle with a circular cross section. The smaller version has a 27 mm diameter cross section.

Below are images of the 3D printed handles in order from left to right and top-down: Ellipse, Finger Grip, Finger Support-Large, Finger Support-Small, Rounded Grip, Sphere-Large, Sphere-Small, Straight-Large, and Straight-Small.

## DESIGN RATIONALE


Files available at https://github.com/makersmakingchange/Adaptive_Utensil_Handles_for_IKEA_IDENTITET | Page 24 of 24

### Opportunities for Improvement

Physical Component / Enclosure
There is one major handle shape that is not currently covered by the 9 handles: a universal cuff handle. Universal cuff adaptive utensils are available on common sites like Amazon, but few provide a larger handle to grip onto, and again, users are unable to test the handle before buying one. Some experimental designs were made for a 3D printed handle compatible with universal cuff straps made in the hospital, but this also does not solve the problem of a high-cost barrier to entry. In the future, a more cost-effective universal cuff handle can be designed to use more readily available strap
materials such as generic fabric, hook-and-loop strips, or even 3D printed TPU.

Another area for improvement is the utensil compatibility. The 2 core models are currently only compatible with the IKEA IDENTITET large spoon and fork. IKEA is a widespread business, but there are still areas of the world that will not have easy access to IKEA products. And if the IDENTITET set is ever discontinued or undergoes design changes, then these 3D printed Adaptive Utensils will no longer be reproducible. As a preventative measure, further tests should be made to develop a core that is able to hold a wider variety of utensil handles. Doing this would further simplify the cores, as the different spoon and fork models could be consolidated as 1 file.

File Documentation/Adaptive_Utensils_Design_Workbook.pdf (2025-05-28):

V2.0.0 | January 2025

# Adaptive Utensil Handles for IKEA IDENTITET

# DESIGN WORKBOOK


© 2024 by Alberta Health Services, Research and Innovation This work is licensed under the CC BY SA 4.0 License: http://creativecommons.org/licenses/by-sa/4.0
Files available at https://github.com/makersmakingchange/Adaptive_Utensil_Handles_for_IKEA_IDENTITET | Page 1 of 37

# Overview

This document contains information on the design of the Adaptive Utensils, a set of adjustable and interchangeable 3D printed adaptive utensil handles.

# for IKEA IDENTITET

# DESIGN WORKBOOK

Files available at https://github.com/makersmakingchange/Adaptive_Utensil_Handles_for_IKEA_IDENTITET | Page 2 of 37

# Contents

Completion Checklist (DELETE BEFORE POSTING) | Error! Bookmark not defined.

## Overview | 1

## Introduction | 3

## Requirements | 3

## Research | 4

## Commercially Available Options | 4

## Special Supplies Adaptive Utensils | 4

## Vincere Silverware Weighted Utensils | 5

## Special Supplies Bendable Adaptive Utensils | 5

## DIY / Maker Friendly Options | 6

## Fork and Spoon Support | 6

## Working Notes | 8

# for IKEA IDENTITET

# DESIGN WORKBOOK

Files available at https://github.com/makersmakingchange/Adaptive_Utensil_Handles_for_IKEA_IDENTITET | Page 3 of 37

# Introduction

Commercially available adaptive utensils are expensive commitments where buyers are unable to trial different styles of handles and determine what best suits their needs. Some purchased sets cannot be returned, which may leave individuals with adaptive utensils that are uncomfortable to use.

The 3D printed Adaptive Utensils play the same role as commercially available adaptive utensils, which is to allow individuals with poor fine motor control to eat independently. However, the 3D printed handles fulfill a different niche in how they are fast and cheap to manufacture, which lowers the barrier-to-entry and lets individuals trial different handle shapes to develop their own preference. Afterwards, users may 3D print more of their preferred handle or purchase a similar commercial adaptive utensil set for long-term usage.

The 3D printed Adaptive Utensils are for individuals who struggle to grasp and manipulate utensils. The affected patient population includes weakness in arm or grip strength, tremors/shakiness, limited range of motion, and poor fine motor skills.

# Requirements

- Handles must be significantly larger than a typical utensil handle and feel ergonomic to hold to

## reduce the strain on fingers

- Must be compatible with at least a spoon and fork.

- There should be as few components as possible to reduce the risk of misplacing them - Handles should be simple and quick to order/manufacture - Utensil must be interchangeable with different types of handles - Adjustable depth for utensil in handle - Adjustable rotation for utensil in handle - Utensil must lock in place during regular usage - Create smooth geometry where possible to improve the overall appearance and feel of the printed handles
- Imitate common shapes for commercial adaptive utensils so users can test those styles before

## buying them

- Printed handle sets must be cheaper than generic commercial adaptive utensils (maximum $30

## CAD per set) - Use PLA and/or PETG, as they are the most common 3D printing materials

# for IKEA IDENTITET

# DESIGN WORKBOOK

Files available at https://github.com/makersmakingchange/Adaptive_Utensil_Handles_for_IKEA_IDENTITET | Page 4 of 37

# Research

## Commercially Available Options

## Special Supplies Adaptive Utensils

Title / Name of device | Special Supplies Adaptive Utensils (4-Piece Kitchen Set) Wide Non-Weighted Non-Slip Handles for Hand Tremors Arthritis Parkinson's or Elderly use | Stainless Steel Knife Fork Spoons - Grey
Link | Amazon Link (https://www.amazon.ca/Adaptive-Utensils-Non-Weighted-Arthritis-Parkinsons/dp/B074JH1T1N?rnid=11192166011&s=hpc)
Author | Brand: Special Supplies. Distributor: Amazon
License | N/A
Cost | $35.00 CAD

Non-weighted adaptive utensils that are dishwasher safe, have stainless-steel utensils, and ribbed silicone handles for improved grip. Each set includes a fork, knife, curved knife, dinner spoon, and soup spoon.

Requirements Met | Requirements Unmet
G01, G02, G03, G04, F04, NF01 | F01, F02, F03, NF02

## Useful Design Features

Utensils are dishwasher safe, which makes cleaning quick and easy.

# for IKEA IDENTITET

# DESIGN WORKBOOK


Files available at https://github.com/makersmakingchange/Adaptive_Utensil_Handles_for_IKEA_IDENTITET | Page 5 of 37

## Vincere Silverware Weighted Utensils

Title / Name of device | Weighted Utensils for Tremors and Parkinsons, Heavy Weight Stainless Steel Silverware Set, Adaptive Eating Flatware Helps Hand Tremors, Parkinsons Aids for Living, Arthritis - Knife, Fork, Spoons, 7oz
Link | Amazon Link (https://www.amazon.ca/Weighted-Utensils-Tremors-Parkinsons-Silverware/dp/B07YNSJDW6?rnid=11192166011&s=hpc)
Author | Brand: Vincere Silverware. Distributor: Amazon
License | N/A
Cost | $99.95 CAD

7oz weighted utensils designed to improve stability for individuals with tremors. They are dishwasher safe, but do not have a significantly larger handle like typical adaptive utensils. Each set includes a knife, fork, tablespoon, and soup spoon.

Requirements Met | Requirements Unmet
G02, G03, G04, F04, NF01 | G01, F01, F02, F03, NF02

## Useful Design Features

The weighted design should help reduce shaky hands from tremors.

## Special Supplies Bendable Adaptive Utensils

Title / Name of device | Special Supplies Adaptive Utensils (4-Piece Kitchen Set) Wide Weighted Non-Slip Handles for Hand Tremors Arthritis Parkinson‚ or Elderly use | Stainless Steel Knife Fork Spoons (Gray Weighted Bendable)
Link | Amazon Link (https://www.amazon.ca/Adaptive-Utensils-Weighted-Arthritis-Parkinsons/dp/B07JCF9HW3?rnid=11192166011&s=hpc)
Author | Brand: Special Supplies. Distributor: Amazon
License | N/A
Cost | $33.40 CAD

# for IKEA IDENTITET

# DESIGN WORKBOOK


Files available at https://github.com/makersmakingchange/Adaptive_Utensil_Handles_for_IKEA_IDENTITET | Page 6 of 37

6oz weighted adaptive utensils that are dishwasher safe, have bendable stainless-steel utensils, and ribbed silicone handles for improved grip. Each set includes a fork, knife, dinner spoon, and soup spoon.

Requirements Met | Requirements Unmet
G01, G02, G03, G04, F03, F04, NF01 | F01, F02, NF02

## Useful Design Features

Utensils are bendable for more user customizability.

## DIY / Maker Friendly Options

<Links to and quick descriptions of DIY / maker friendly devices that may meet a user’s needs>

## Fork and Spoon Support

Title | Fork and Spoon Support
Link | Makers Making Change Link (https://www.makersmakingchange.com/s/product/fork-and-spoon-support/01tJR00000068zYYAQ)
Author | MMC Community
License | Attribution-NonCommercial-ShareAlike4.0 International
Cost | $0-$10 CAD
Test Build (Y/N) | N
Add to Library (Y/N) | Already Added

# for IKEA IDENTITET

# DESIGN WORKBOOK


Files available at https://github.com/makersmakingchange/Adaptive_Utensil_Handles_for_IKEA_IDENTITET | Page 7 of 37

The Fork and Spoon Support allows people with limited grip strength to hold and use eating utensils. Users can slot the device over their palm for a grip-free usage or hold both handles for a larger grip. The slot fits standard sized eating utensils like forks, spoons, and knives.

Requirements Met | Requirements Unmet
G01, G02, G03, G04, F02, F04, NF01 | F01, F03, NF02

## Useful Design Features

Compatible with a wide variety of utensils. Clips around the hand and does not require individuals to grip anything.

## Universal hand grip for cutlery

Title | Universal hand grip for cutlery
Link | Thingiverse Link (https://www.thingiverse.com/thing:686084)
Author | Pole_ergo
License | Creative Commons – Attribution – Non-commercial 4.0 International
Cost | $0-$10 CAD
Test Build (Y/N) | N
Add to Library (Y/N) | N

# for IKEA IDENTITET

# DESIGN WORKBOOK

Files available at https://github.com/makersmakingchange/Adaptive_Utensil_Handles_for_IKEA_IDENTITET | Page 8 of 37

3D printed handle for flat metal fork/spoon/knife. Must be printed in a soft material like Ninjaflex, where infill density will affect the overall rigidity of the handle.

Requirements Met | Requirements Unmet
G01, G02, G03, G04, F02, F04, NF01 | F01, F03, NF02

## Useful Design Features

Soft material makes the handle compatible with a wide variety of utensil handles and makes the outer shell conform to the user’s grip.

# Working Notes

Students who worked on this project wrote digital notes of the development process. Screenshots from each student’s working notes have been inserted below.

# for IKEA IDENTITET

# DESIGN WORKBOOK


Files available at https://github.com/makersmakingchange/Adaptive_Utensil_Handles_for_IKEA_IDENTITET | Page 9 of 37

## Handover from Fall 2022

# for IKEA IDENTITET

# DESIGN WORKBOOK


Files available at https://github.com/makersmakingchange/Adaptive_Utensil_Handles_for_IKEA_IDENTITET | Page 10 of 37

# for IKEA IDENTITET

# DESIGN WORKBOOK


Files available at https://github.com/makersmakingchange/Adaptive_Utensil_Handles_for_IKEA_IDENTITET | Page 11 of 37

## Progress & Handover from April 2024

# for IKEA IDENTITET

# DESIGN WORKBOOK

Files available at https://github.com/makersmakingchange/Adaptive_Utensil_Handles_for_IKEA_IDENTITET | Page 12 of 37

# for IKEA IDENTITET

# DESIGN WORKBOOK


Files available at https://github.com/makersmakingchange/Adaptive_Utensil_Handles_for_IKEA_IDENTITET | Page 13 of 37

# for IKEA IDENTITET

# DESIGN WORKBOOK


Files available at https://github.com/makersmakingchange/Adaptive_Utensil_Handles_for_IKEA_IDENTITET | Page 14 of 37

# for IKEA IDENTITET

# DESIGN WORKBOOK


Files available at https://github.com/makersmakingchange/Adaptive_Utensil_Handles_for_IKEA_IDENTITET | Page 15 of 37

# for IKEA IDENTITET

# DESIGN WORKBOOK

Files available at https://github.com/makersmakingchange/Adaptive_Utensil_Handles_for_IKEA_IDENTITET | Page 16 of 37

# for IKEA IDENTITET

# DESIGN WORKBOOK

Files available at https://github.com/makersmakingchange/Adaptive_Utensil_Handles_for_IKEA_IDENTITET | Page 17 of 37

# for IKEA IDENTITET

# DESIGN WORKBOOK


Files available at https://github.com/makersmakingchange/Adaptive_Utensil_Handles_for_IKEA_IDENTITET | Page 18 of 37

# for IKEA IDENTITET

# DESIGN WORKBOOK


Files available at https://github.com/makersmakingchange/Adaptive_Utensil_Handles_for_IKEA_IDENTITET | Page 19 of 37

# for IKEA IDENTITET

# DESIGN WORKBOOK


Files available at https://github.com/makersmakingchange/Adaptive_Utensil_Handles_for_IKEA_IDENTITET | Page 20 of 37

# for IKEA IDENTITET

# DESIGN WORKBOOK

Files available at https://github.com/makersmakingchange/Adaptive_Utensil_Handles_for_IKEA_IDENTITET | Page 21 of 37

# for IKEA IDENTITET

# DESIGN WORKBOOK


Files available at https://github.com/makersmakingchange/Adaptive_Utensil_Handles_for_IKEA_IDENTITET | Page 22 of 37

# for IKEA IDENTITET

# DESIGN WORKBOOK


Files available at https://github.com/makersmakingchange/Adaptive_Utensil_Handles_for_IKEA_IDENTITET | Page 23 of 37

# for IKEA IDENTITET

# DESIGN WORKBOOK


Files available at https://github.com/makersmakingchange/Adaptive_Utensil_Handles_for_IKEA_IDENTITET | Page 24 of 37

# for IKEA IDENTITET

# DESIGN WORKBOOK

Files available at https://github.com/makersmakingchange/Adaptive_Utensil_Handles_for_IKEA_IDENTITET | Page 25 of 37

## Progress from December 2024

# for IKEA IDENTITET

# DESIGN WORKBOOK

Files available at https://github.com/makersmakingchange/Adaptive_Utensil_Handles_for_IKEA_IDENTITET | Page 26 of 37

# for IKEA IDENTITET

# DESIGN WORKBOOK


Files available at https://github.com/makersmakingchange/Adaptive_Utensil_Handles_for_IKEA_IDENTITET | Page 27 of 37

# for IKEA IDENTITET

# DESIGN WORKBOOK


Files available at https://github.com/makersmakingchange/Adaptive_Utensil_Handles_for_IKEA_IDENTITET | Page 28 of 37

# for IKEA IDENTITET

# DESIGN WORKBOOK

Files available at https://github.com/makersmakingchange/Adaptive_Utensil_Handles_for_IKEA_IDENTITET | Page 29 of 37

# for IKEA IDENTITET

# DESIGN WORKBOOK


Files available at https://github.com/makersmakingchange/Adaptive_Utensil_Handles_for_IKEA_IDENTITET | Page 30 of 37

# for IKEA IDENTITET

# DESIGN WORKBOOK

Files available at https://github.com/makersmakingchange/Adaptive_Utensil_Handles_for_IKEA_IDENTITET | Page 31 of 37

# for IKEA IDENTITET

# DESIGN WORKBOOK


Files available at https://github.com/makersmakingchange/Adaptive_Utensil_Handles_for_IKEA_IDENTITET | Page 32 of 37

# for IKEA IDENTITET

# DESIGN WORKBOOK


Files available at https://github.com/makersmakingchange/Adaptive_Utensil_Handles_for_IKEA_IDENTITET | Page 33 of 37

# for IKEA IDENTITET

# DESIGN WORKBOOK


Files available at https://github.com/makersmakingchange/Adaptive_Utensil_Handles_for_IKEA_IDENTITET | Page 34 of 37

# for IKEA IDENTITET

# DESIGN WORKBOOK

Files available at https://github.com/makersmakingchange/Adaptive_Utensil_Handles_for_IKEA_IDENTITET | Page 35 of 37

# for IKEA IDENTITET

# DESIGN WORKBOOK


Files available at https://github.com/makersmakingchange/Adaptive_Utensil_Handles_for_IKEA_IDENTITET | Page 36 of 37

# for IKEA IDENTITET

# DESIGN WORKBOOK


Files available at https://github.com/makersmakingchange/Adaptive_Utensil_Handles_for_IKEA_IDENTITET | Page 37 of 37

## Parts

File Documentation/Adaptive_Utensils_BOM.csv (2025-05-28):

Device: | Adaptive Utensils
Version: | V2.0.0
Last Updated: | 2025-May-28
 |  |  |  |  |  |  |  | Total filament (g) |  | Unit Cost | Total Estimated Cost
 |  |  |  |  |  |  |  | 351.74 |  | $11.51 | $19.00
ID | Commercial Parts |  |  |  |  |  |  |  |  | $2.50 | $9.99
 | Part | Description |  | Manufacturer | Supplier | QTY / Device | QTY / PKG | PKGs | $/ PKG | $ / Device | Total Estimated Cost | Link
 | IDENTITET Spoon and Fork | 16-piece cutlery set. Stainless steel, dishwasher safe. Includes: Fork, knife, spoon, and teaspoon, 4 of each. |  | IKEA | IKEA | 1 | 4 | 1 | $9.99 | $2.50 | $9.99 | https://www.ikea.com/ca/en/p/identitet-16-piece-cutlery-set-stainless-steel-50578174/
 | 3D Printed Parts |  |  |  |  |  |  | 355.32 |  | $9.01 | $9.01
 | Part | Description | Filament Type | Filament | Color | QTY / Device | Mass (g) / Part | Total Mass | $ / kg | $ / Device | Total Estimated Cost | Link
 | IKEA_Core-Fork | Core that wraps around the IKEA IDENTITET large fork. Allows the fork to be swapped and locked between handle types. Commonly printed in black PETG. | PetG |  | Black | 1 | 9.06 | 9.06 | $30.00 | $0.27 | $0.27
 | IKEA_Core-Spoon | Core that wraps around the IKEA IDENTITET large spoon. Allows the spoon to be swapped and locked between handle types. Commonly printed in white PETG. | PetG |  | White | 1 | 8.99 | 8.99 | $30.00 | $0.27 | $0.27
 | IKEA_Shell | Outer shell slides around the fork and spoon cores to hold them closed. The outer shell is interchangeable between fork and spoon cores. | PetG |  | Any | 2 | 3.58 | 7.16 | $30.00 | $0.21 | $0.21
 | IKEA_Ellipse | Cylinder handle with an oval cross section shape. | PLA |  | Any | 1 | 32.78 | 32.78 | $25.00 | $0.82 | $0.82
 | IKEA_FingerGrip | Handle with finger groove indentations. | PLA |  | Any | 1 | 25.65 | 25.65 | $25.00 | $0.64 | $0.64
 | IKEA_FingerSupport-Large | Has rigid support around the fingers and thumb. The larger version has a 33mm spacing for the finger support. | PLA |  | Any | 1 | 50.84 | 50.84 | $25.00 | $1.27 | $1.27
 | IKEA_FingerSupport-Small | Has rigid support around the fingers and thumb. The smaller version has a 27mm spacing for the finger support. | PLA |  | Any | 1 | 50.19 | 50.19 | $25.00 | $1.25 | $1.25
 | IKEA_RoundedGrip | Rounded handle that is thickest in the middle and tapers thinner at the top and bottom. | PLA |  | Any | 1 | 30.29 | 30.29 | $25.00 | $0.76 | $0.76
 | IKEA_Sphere-Large | Spherical handle. The larger version has a 70 mm diameter sphere. | PLA |  | Any | 1 | 45.38 | 45.38 | $25.00 | $1.13 | $1.13
 | IKEA_Sphere-Small | Spherical handle. The smaller version has a 52 mm diameter sphere. | PLA |  | Any | 1 | 20.85 | 20.85 | $25.00 | $0.52 | $0.52
 | IKEA_Straight-Large | Cylinder handle with a circular cross section. The larger version has a 42 mm diameter cross section. | PLA |  | Any | 1 | 48.98 | 48.98 | $25.00 | $1.22 | $1.22
 | IKEA_Straight-Small | Cylinder handle with a circular cross section. The smaller version has a 27 mm diameter cross section. | PLA |  | Any | 1 | 25.15 | 25.15 | $25.00 | $0.63 | $0.63
 | Custom PCB |  |  |  |  |  |  |  |  | $- | $-
 | Part | Description |  | Manufacturer | Supplier | QTY / Device | QTY / PKG | PKGs | $/ PKG | $ / Device | Total Estimated Cost | Link
 | N/A
 | Tools
 | Tool | Description |  | Manufacturer | Supplier |  |  |  |  |  |  | Link
 | Alternatives
 | Part | Description |  | Manufacturer | Supplier | QTY / Device | QTY / PKG | PKGs | $/ PKG | $ / Device | Total Estimated Cost | Link

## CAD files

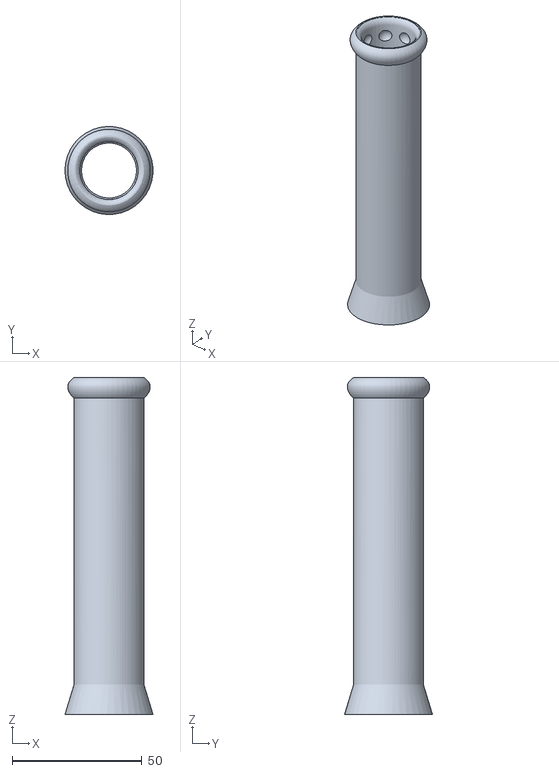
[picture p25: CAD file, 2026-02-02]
Build_Files/3D_Printing_Files/IKEA_Straight-Small.STL
34.0 x 34.0 x 130.0

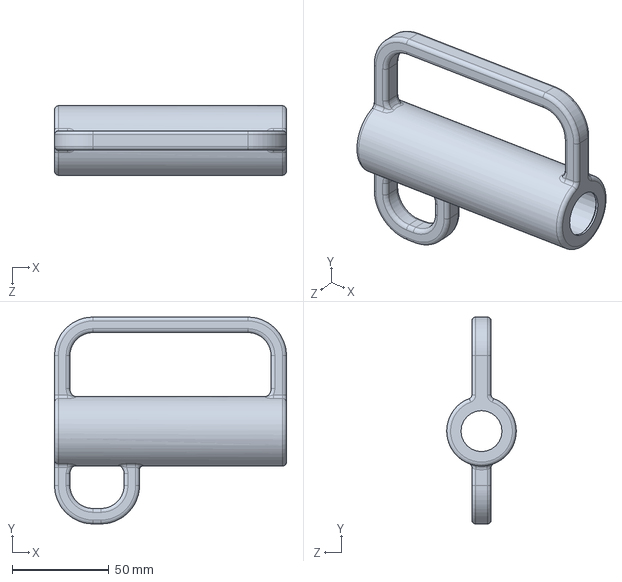
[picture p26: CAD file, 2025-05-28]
Design_Files/CAD_Design_Files/SolidWorks/IKEA_FingerSupport-Large_Rev02.SLDPRT
120.0 x 107.0 x 36.0 mm

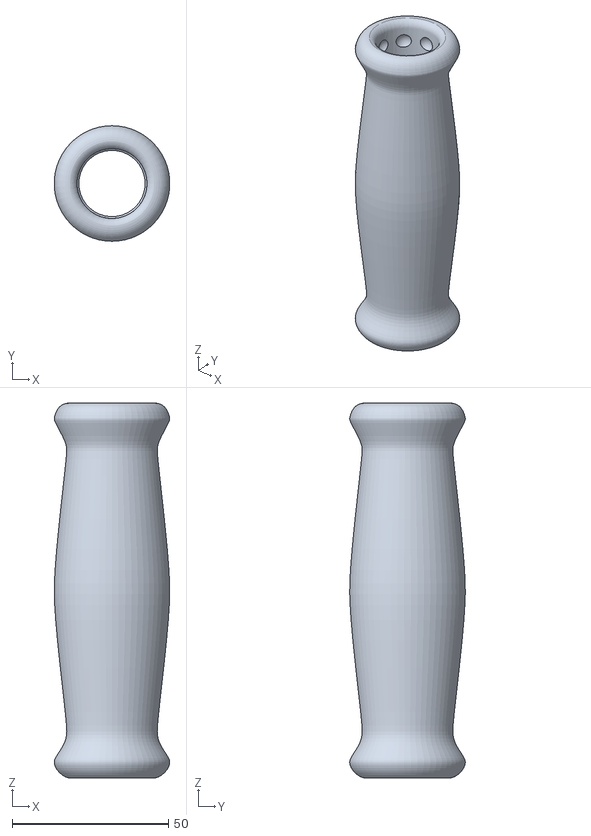
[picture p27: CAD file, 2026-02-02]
Build_Files/3D_Printing_Files/IKEA_RoundedGrip.STL
36.9 x 37.0 x 120.0

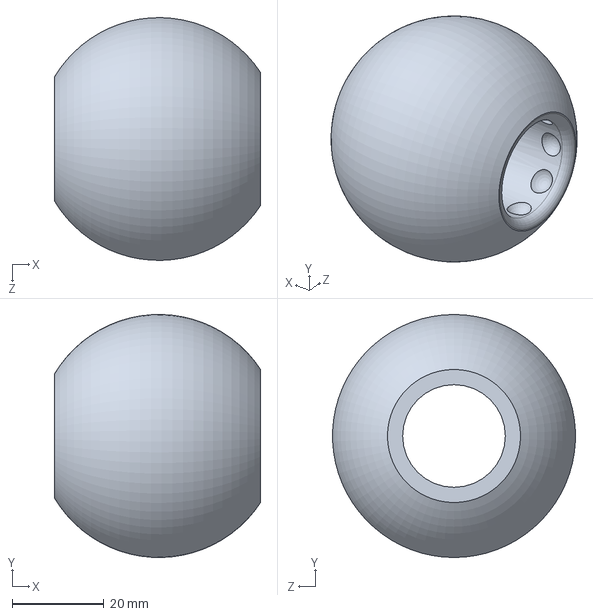
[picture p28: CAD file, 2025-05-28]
Design_Files/CAD_Design_Files/SolidWorks/IKEA_Sphere-Small_Rev02.SLDPRT
45.0 x 53.0 x 52.9 mm

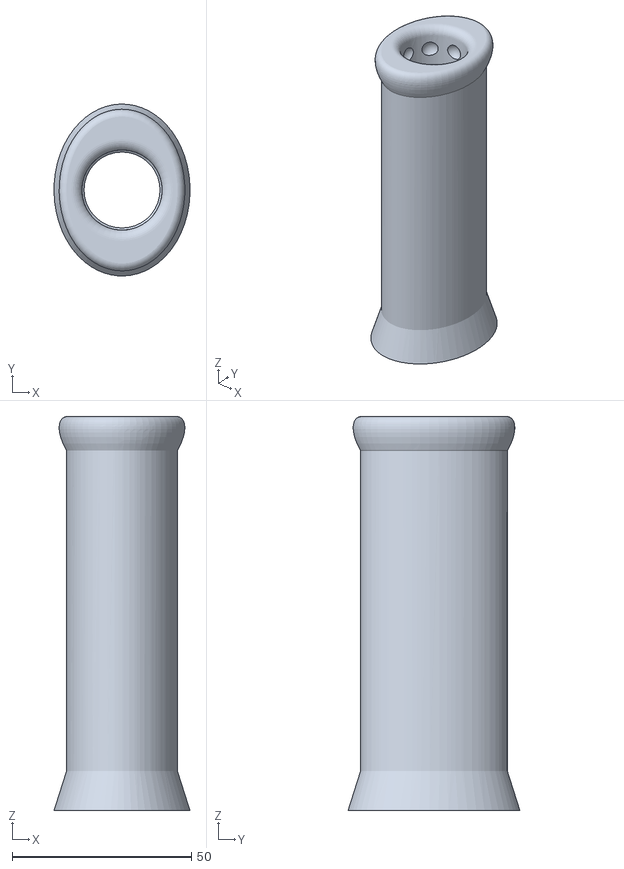
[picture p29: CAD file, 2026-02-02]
Build_Files/3D_Printing_Files/IKEA_Ellipse.STL
38.0 x 48.0 x 110.0

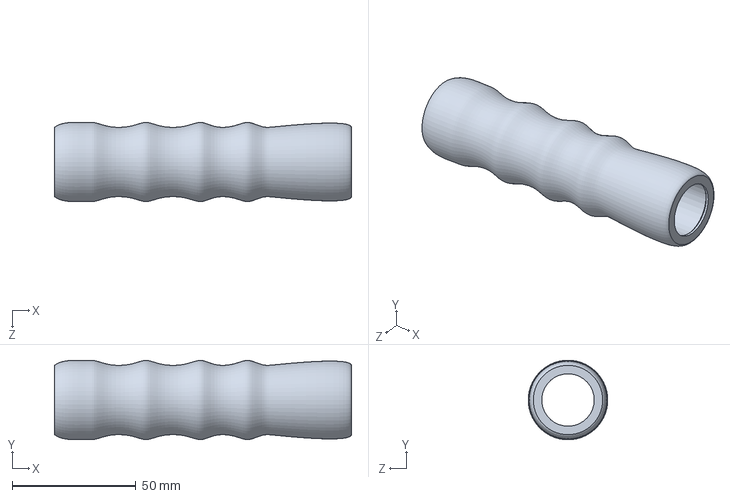
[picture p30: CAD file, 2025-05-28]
Design_Files/CAD_Design_Files/SolidWorks/IKEA_FingerGrip_Rev02.SLDPRT
120.0 x 32.1 x 32.1 mm

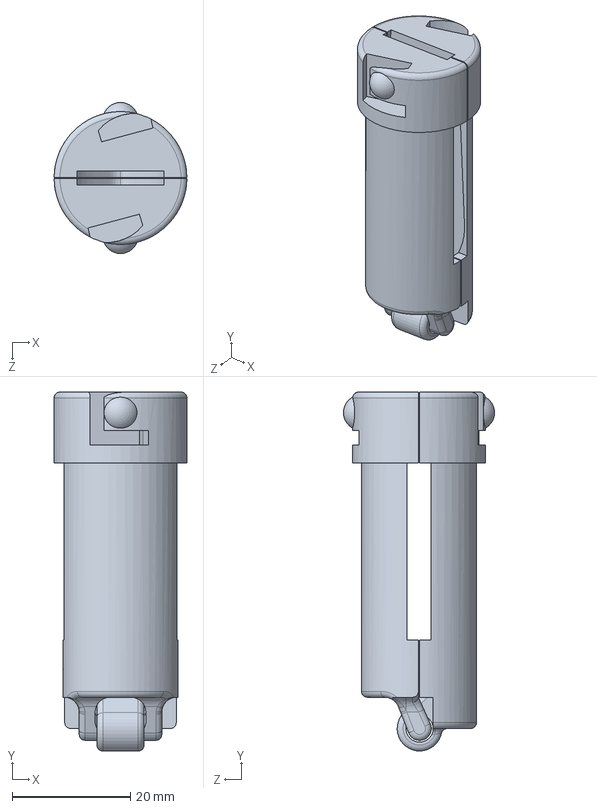
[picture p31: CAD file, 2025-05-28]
Design_Files/CAD_Design_Files/SolidWorks/IKEA_Core_Rev02.SLDPRT
22.5 x 60.8 x 25.6 mm

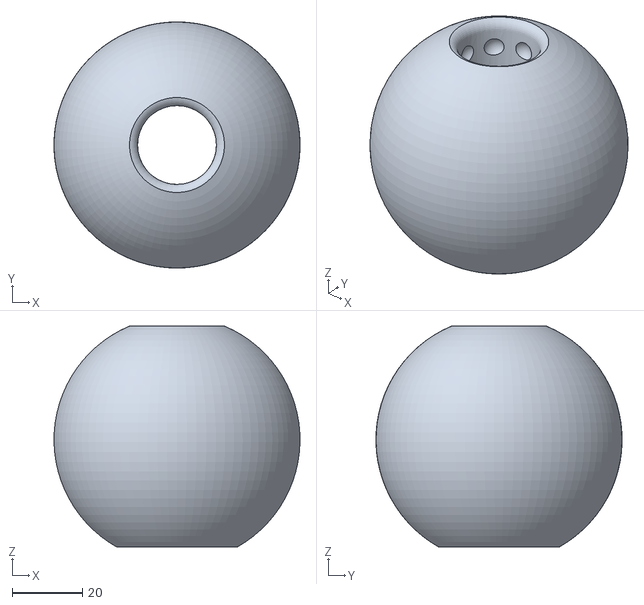
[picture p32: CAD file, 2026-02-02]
Build_Files/3D_Printing_Files/IKEA_Sphere-Large.STL
69.9 x 70.0 x 62.8

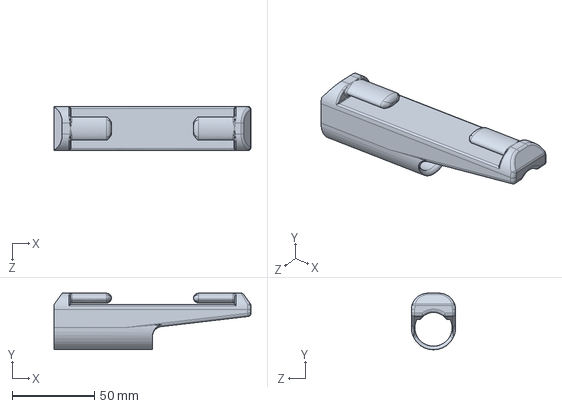
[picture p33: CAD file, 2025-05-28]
Design_Files/CAD_Design_Files/SolidWorks/IKEA_Velcro_Rev02.SLDPRT
120.0 x 34.5 x 27.0 mm

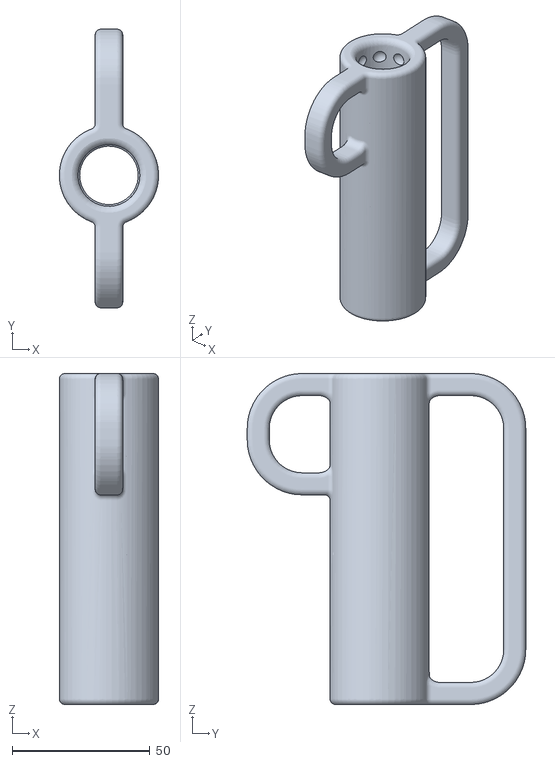
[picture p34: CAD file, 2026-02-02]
Build_Files/3D_Printing_Files/IKEA_FingerSupport-Small.STL
36.0 x 101.0 x 120.0

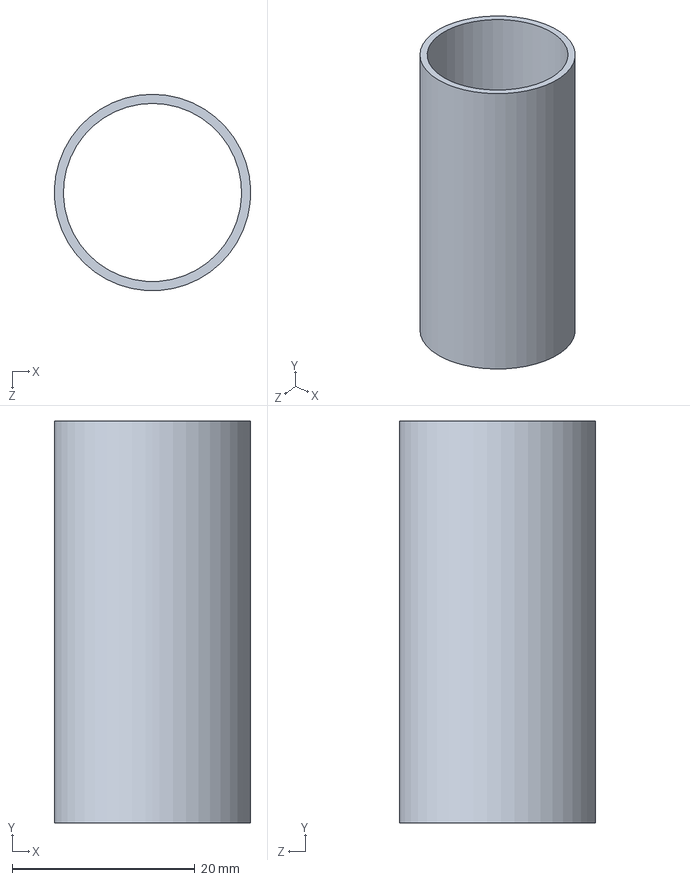
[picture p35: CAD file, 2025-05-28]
Design_Files/CAD_Design_Files/SolidWorks/IKEA_Shell_Rev02.SLDPRT
21.5 x 44.0 x 21.5 mm

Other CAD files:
Build_Files/3D_Printing_Files/IKEA_Sphere-Small.STL
Build_Files/3D_Printing_Files/IKEA_FingerSupport-Large.STL
Design_Files/CAD_Design_Files/SolidWorks/IKEA_RoundedGrip_Rev02.SLDPRT
Design_Files/CAD_Design_Files/SolidWorks/IKEA_Sphere-Large_Rev02.SLDPRT
Build_Files/3D_Printing_Files/IKEA_Core-Fork.STL
Design_Files/CAD_Design_Files/SolidWorks/IKEA_Ellipse_Rev02.SLDPRT
Build_Files/3D_Printing_Files/IKEA_Core-Spoon.STL
Build_Files/3D_Printing_Files/IKEA_FingerGrip.STL
Build_Files/3D_Printing_Files/IKEA_Shell.STL
Build_Files/3D_Printing_Files/IKEA_Straight-Large.STL
Build_Files/3D_Printing_Files/IKEA_Velcro.STL
Design_Files/CAD_Design_Files/SolidWorks/IKEA_FingerSupport-Small_Rev02.SLDPRT
Design_Files/CAD_Design_Files/SolidWorks/IKEA_Straight-Large_Rev02.SLDPRT
Design_Files/CAD_Design_Files/SolidWorks/IKEA_Straight-Small_Rev02.SLDPRT

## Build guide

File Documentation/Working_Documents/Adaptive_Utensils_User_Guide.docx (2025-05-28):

# Overview

This document contains the necessary information to use the Adaptive Utensils, a set of adjustable and interchangeable 3D printed adaptive utensil handles.


## Introduction

Commercially available adaptive utensils are expensive commitments where buyers are unable to trial different styles of handles and determine what best suits their needs. Some purchased sets cannot be returned, which may leave individuals with adaptive utensils that are uncomfortable to use.

The 3D printed Adaptive Utensils play the same role as commercially available adaptive utensils, which is to allow individuals with poor fine motor control to eat independently. However, the 3D printed handles fulfill a different niche in how they are fast and cheap to manufacture, which lowers the barrier-to-entry and lets individuals trial different handle shapes to develop their own preference. Afterwards, users may 3D print more of their preferred handle or purchase a similar commercial adaptive utensil set for long-term usage.

The 3D printed Adaptive Utensils are for individuals who struggle to grasp and manipulate utensils. The affected patient population includes weakness in arm or grip strength, tremors/shakiness, limited range of motion, and poor fine motor skills.

## Features

There are 3 main components to this design: IKEA IDENTITET utensils, 3D printed handles, and 3D printed core assemblies to interface between the utensils and handles.

The core assemblies consist of two parts, where the core part is designed to clamp around the utensil bases while a separate shell can slide around the core clamp to lock it closed. The cores have 2 separate models with specific slot cutouts to hold the IKEA IDENTITET large spoon and fork profiles. Separate colors help differentiate the core profiles, so the spoon core is commonly printed with white PETG and the fork core is commonly printed with black PETG. Otherwise, the core types can be labeled with a permanent marker.

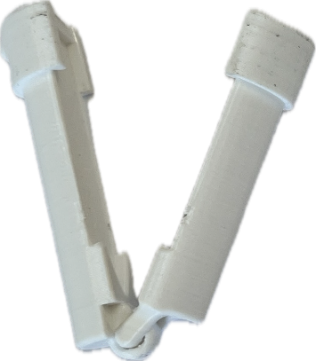
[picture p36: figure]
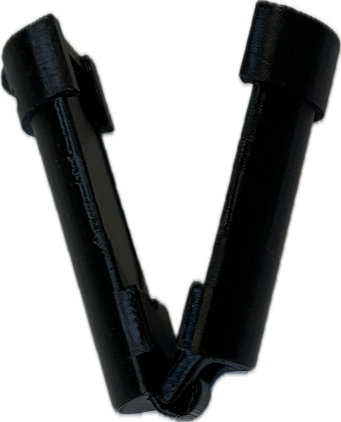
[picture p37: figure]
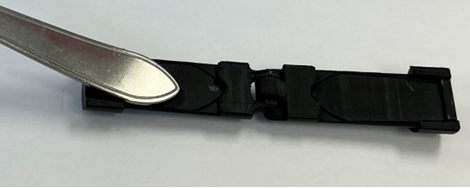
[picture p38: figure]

Once together with the proper utensil, the core assemblies can be inserted into any of the 3D printed handles. The core's ball socket mechanism correlates to 24 hemisphere cutouts in the handles such that the utensils can be locked in the handle while still allowing adjustment and removal when sufficient force is applied to the utensil. The cutouts are arranged in 3 rings of 8, which allow for 3 levels of depth adjustment in increments of 20mm and for 8 levels of rotation adjustment in increments of 45°.

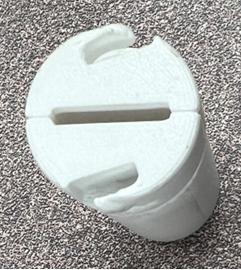
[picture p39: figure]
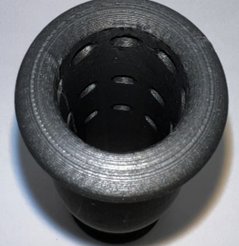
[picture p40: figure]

Below are two images demonstrating the depth and angular adjustment range of the cores:

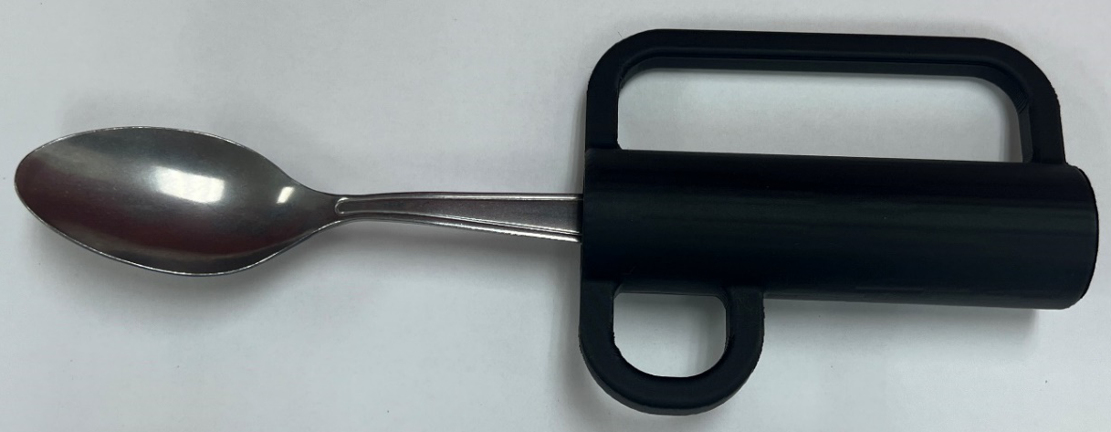
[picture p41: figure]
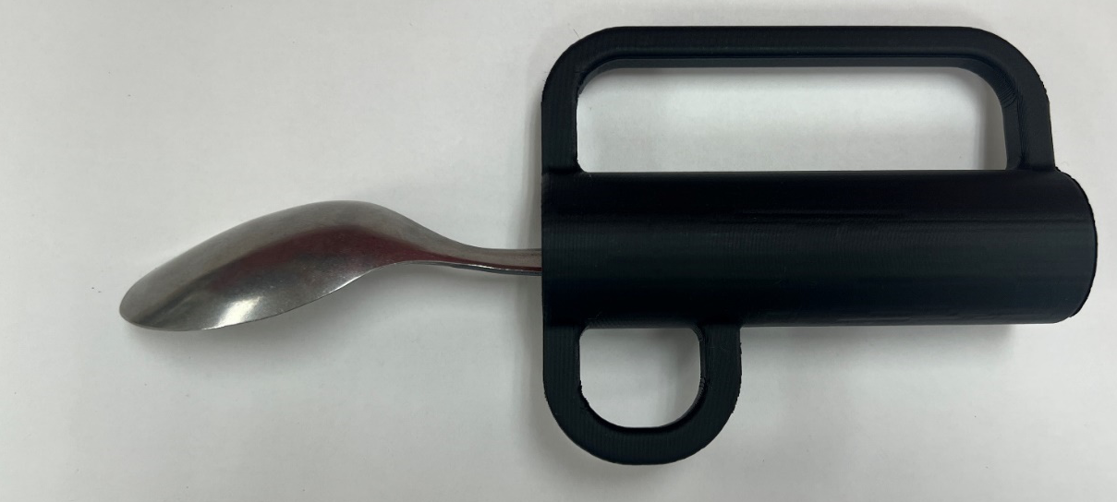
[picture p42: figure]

Each of the handles offer a large, smooth area to grasp for improved ergonomics. Some handles mimic common shapes for commercial adaptive utensils, and others have more experimental shapes to explore the possibilities of 3D printing with adaptive utensils. All the 9 handle types for the 3D printed Adaptive Utensils are listed below:

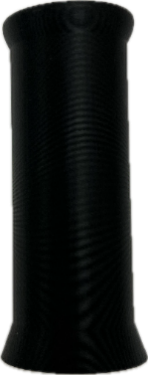
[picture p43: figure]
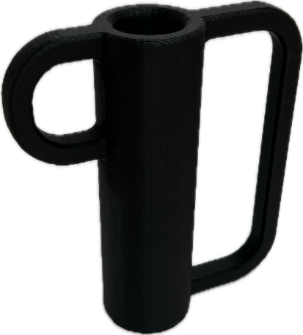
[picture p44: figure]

Ellipse (Cylinder handle with an oval cross section shape) | Finger Grip (Handle with finger groove indentations) | Finger Support-Large (Rigid support around the fingers; 33mm spacing)

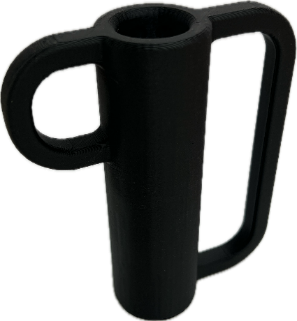
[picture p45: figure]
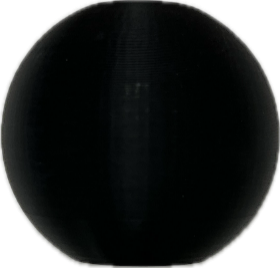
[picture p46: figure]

Finger Support-Small (Rigid support around the fingers; 27mm spacing) | Rounded Grip (Thickest in the middle and tapers thinner at the top and bottom) | Sphere-Large (Spherical handle; 70 mm diameter)

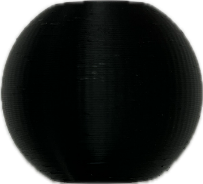
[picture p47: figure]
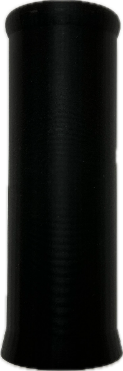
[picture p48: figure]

Sphere-Small (Spherical handle; 52 mm diameter) | Straight-Large (Cylinder handle with a circular cross section; 42 mm diameter) | Straight-Small (Cylinder handle with a circular cross section; 27 mm diameter)

## Specifications

Part | Item | Adaptive Utensils
Fork (IKEA IDENTITET) | Maximum Handle Extension Length [mm] | 145
| Mass [g] | 34.5
Spoon (IKEA IDENTITET) | Maximum Handle Extension Length [mm] | 140
| Mass [g] | 38.9
Fork Core | Size (Length x Width x Height) [mm] | 26 x 23 x 61
| Mass [g] | 9.06
Spoon Core | Size (Length x Width x Height) [mm] | 26 x 23 x 61
| Mass [g] | 8.99
Shell | Size (Length x Width x Height) [mm] | 22 x 22 x 44
| Mass [g] | 3.58
Ellipse | Size (Length x Width x Height) [mm] | 38 x 48 x 110
| Mass [g] | 32.78
Finger Grip | Size (Length x Width x Height) [mm] | 32 x 32 x 120
| Mass [g] | 25.65
Finger Support – Large | Size (Length x Width x Height) [mm] | 36 x 107 x 120
| Mass [g] | 50.84
Finger Support – Small | Size (Length x Width x Height) [mm] | 36 x 101 x 120
| Mass [g] | 50.19
Rounded Grip | Size (Length x Width x Height) [mm] | 37 x 37 x 120
| Mass [g] | 30.29
Sphere – Large | Size (Length x Width x Height) [mm] | 70 x 70 x 63
| Mass [g] | 45.38
Sphere – Small | Size (Length x Width x Height) [mm] | 53 x 53 x 45
| Mass [g] | 20.85
Straight – Large | Size (Length x Width x Height) [mm] | 46 x 46 x 130
| Mass [g] | 48.98
Straight – Small | Size (Length x Width x Height) [mm] | 34 x 34 x 130
| Mass [g] | 25.15

## Compatibility

The core assemblies are only compatible to hold the IKEA IDENTITET large spoon and fork and can only be inserted into the 3D printed handles included with this device.

## Usage

### Initial Setup

Assemble the cores with the IKEA utensils and shells, then insert them into a 3D printed handle at the desired position. Make sure the core assembly locks into a socket before use.

### Regular Use

Once assembled, the 3D Printed Adaptive Utensils may be used as a regular utensil to eat.

### Takedown / Storage

When not in use, the Adaptive Utensils should be stored in a cool place out of direct sunlight.

## Care

The Adaptive Utensils is made of 3D printed plastic. Exposure to high heat may cause warping and/or negatively affect function. Extended exposure to sunlight will also weaken the plastic on the device. Please dry the 3D printed parts after washing.

### Cleaning

The Adaptive Utensils can be wiped with a damp cloth. The Adaptive Utensils can also be cleaned by scrubbing with warm water and dish soap. Do not use hot water or clean in a dishwasher.

## Disposal

PLA filament may be industrially compostable in your area. Check with your waste management company if PLA can be composted or must be thrown in the garbage.

Disassemble the Adaptive Utensils and separate out the recyclable and compostable components, and those that must be thrown out.

© 2024 by Alberta Health Services, Research and Innovation This work is licensed under the CC BY SA 4.0 License: http://creativecommons.org/licenses/by-sa/4.0 Files available at https://github.com/makersmakingchange/Adaptive_Utensil_Handles_for_IKEA_IDENTITET Page 2 of 3

V2.0.0 | January 2025 Adaptive Utensils User Guide

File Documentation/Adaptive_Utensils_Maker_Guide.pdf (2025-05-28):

V2.0.0 | January 2025

## Adaptive Utensil Handles for IKEA IDENTITET

## MAKER GUIDE

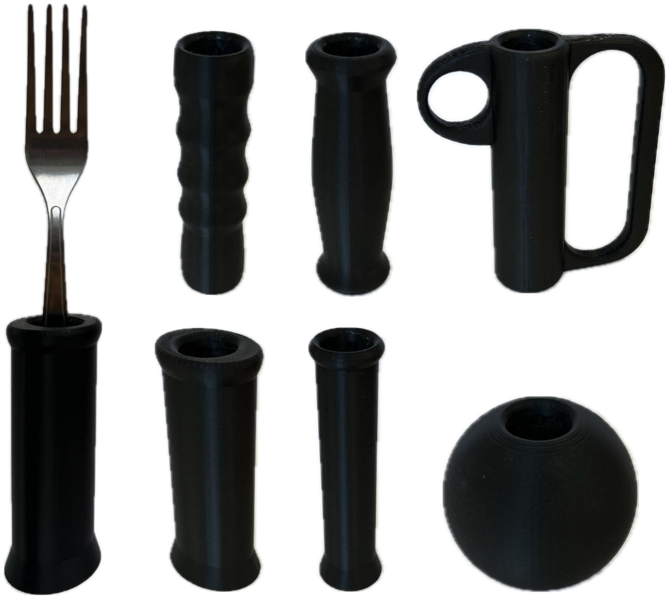
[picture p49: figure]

© 2024 by Alberta Health Services, Research and Innovation This work is licensed under the CC BY SA 4.0 License: http://creativecommons.org/licenses/by-sa/4.0
Files available at https://github.com/makersmakingchange/Adaptive_Utensil_Handles_for_IKEA_IDENTITET | Page 1 of 15

### Overview

This document contains the necessary information to build the Adaptive Utensils, a set of adjustable and interchangeable 3D printed adaptive utensil handles.

## for IKEA IDENTITET

## MAKER GUIDE

Files available at https://github.com/makersmakingchange/Adaptive_Utensil_Handles_for_IKEA_IDENTITET | Page 2 of 15

### Contents

Overview | 1
Maker Checklist | 3
Maker To Do List | 3
Items to Give to User | 3
Tool List | 4
Tools / Equipment | 4
Supplies | 4
Personal Protective Equipment (PPE) | 4
Customization Guide | 5
3D Printing Guide | 5
3D Printing Summary | 5
3D Printing Settings | 5
Post-Processing | 6
Examples of Quality Prints | 7
Maker Component List | 9
Assembly Guide | 11
Part A: 3D Printed Adaptive Utensils | 12
Part A: Required Components | 12
Part A: Required Tools and Supplies | 13
Part A: Required Personal Protective Equipment (PPE) | 13
Part A: 3D Printed Adaptive Utensils Assembly Steps | 13
Testing | 15
Troubleshooting | 15

## for IKEA IDENTITET

## MAKER GUIDE

Files available at https://github.com/makersmakingchange/Adaptive_Utensil_Handles_for_IKEA_IDENTITET | Page 3 of 15

### Maker Checklist

This list provides an overview of the steps required to build and deliver the 3D Printed Adaptive Utensils.

### Maker To Do List

Read through the Maker Guide to become familiar with required components, tools, supplies, safety gear, and overall assembly steps.
Talk to the User about customization options
- Handle type, size, and quantity (Ellipse, Finger Grip, Finger Support-Large/Small, Rounded Grip, Sphere-Large/Small, Straight-Large/Small)
- Number and types of core assemblies (Spoon or Fork Core)
- Print color
- How they would like to receive the “User Guide” (PDF or physical copy) Order hardware components
Gather tools, supplies, and safety equipment.
Assemble the device
Test the 3D Printed Adaptive Utensils
Print “User Guide” (if the User would like a physical copy)

### Items to Give to User

The desired handle types in the correct size and quantity (Ellipse, Finger Grip, Finger Support-Large/Small, Rounded Grip, Sphere-Large/Small, Straight-Large/Small)
Spoon and fork core assemblies (each assembly consists of 1 core and 1 shell part)
IKEA IDENTITET large spoon and fork utensils
Note: All cores and handles should be tested for assembly and adjustability before giving to user, however they may be disassembled for easier transportation
“User Guide”

## for IKEA IDENTITET

## MAKER GUIDE

Files available at https://github.com/makersmakingchange/Adaptive_Utensil_Handles_for_IKEA_IDENTITET | Page 4 of 15

### Tool List

### Tools / Equipment

Tool ID | Description | Required / Recommended | Notes
T01 | 3D printer | Required | To manufacture the 3D Printed Adaptive Utensils
T02 | Putty knife or similar scraper | Recommended | To remove small or thin parts from the build plate
T03 | Flush cutters or pliers | Recommended | To remove support

### Supplies

Supplies ID Description | Quantity | Notes
S01 | PLA Filament | 326.53g | For 3D printing the handles
S02 | PETg Filament | 25.21g | For 3D printing the spoon/fork cores and the core shells

### Personal Protective Equipment (PPE)

PPE ID | Description | Notes
P01 | Safety Glasses | To protect eyes against occasional flying filament when removing supports

## for IKEA IDENTITET

## MAKER GUIDE

Files available at https://github.com/makersmakingchange/Adaptive_Utensil_Handles_for_IKEA_IDENTITET | Page 5 of 15

### Customization Guide

There are separate STL files for different size options of certain handle types. The handles and cores may be printed in the user’s desired color.

### 3D Printing Guide

The device was originally printed on a BambuLab X1-Carbon using Bambu Studio.

Used default settings with 0.2mm layer height and a 0.4mm nozzle for both PLA and PETG filament on a textured PEI build plate. Enabled tree supports for relevant files.

### 3D Printing Summary

To print a full set of handles and cores (one copy of each handle file, both types of cores, and two shells)

Metrics | Single Unit
Total Print Time (hour min) | 17h29
Total Number of Components | 13
Typical Total Mass (g) | 351.74g
Typical Number of Print Setups | 5

### 3D Printing Settings

Note that the 3D printing material should be assumed to be PLA unless otherwise noted in the table below.

Print File Name | Qty | Total Print Time (hr:min) | Mass (g) | Infill (%) | Support (Y/N) | Layer Height/ Nozzle Diameter(mm) | Notes
Adaptive_Utensils_IKEA _Core-Fork | 1 | 1:10 | 9.06 | 15 | Y | 0.2mm Layer Height, 0.4mm Nozzle Diameter | PETg
Adaptive_Utensils_IKEA _Core-Spoon | 1 | 1:10 | 8.99 | 15 | Y | 0.2mm Layer Height, 0.4mm Nozzle Diameter | PETg
Adaptive_Utensils_IKEA _Shell | 2 | 0:52 | 7.16 | 15 | N | 0.2mm Layer Height, 0.4mm Nozzle Diameter | PLA
Adaptive_Utensils_IKEA _Ellipse | 1 | 1:32 | 32.78 | 15 | N | 0.2mm Layer Height, 0.4mm Nozzle Diameter | PLA
Adaptive_Utensils_IKEA _FingerGrip | 1 | 1:34 | 25.65 | 15 | N | 0.2mm Layer Height, 0.4mm Nozzle Diameter | PLA

## for IKEA IDENTITET

## MAKER GUIDE

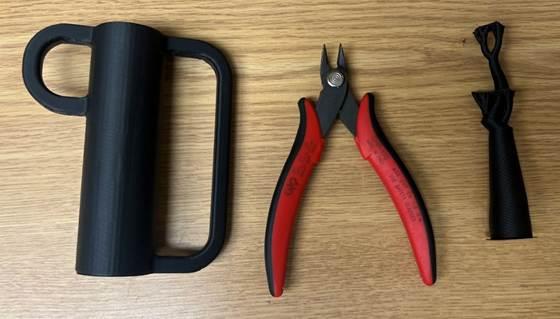
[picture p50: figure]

Files available at https://github.com/makersmakingchange/Adaptive_Utensil_Handles_for_IKEA_IDENTITET | Page 6 of 15
Adaptive_Utensils_IKEA _FingerSupport-Large | 1 | 2:01 | 50.84 | 15 | Y | 0.2mm Layer Height, 0.4mm Nozzle Diameter | PLA
Adaptive_Utensils_IKEA _FingerSupport-Small | 1 | 2:00 | 50.19 | 15 | Y | 0.2mm Layer Height, 0.4mm Nozzle Diameter | PLA
Adaptive_Utensils_IKEA _RoundedGrip | 1 | 1:36 | 30.29 | 15 | N | 0.2mm Layer Height, 0.4mm Nozzle Diameter | PLA
Adaptive_Utensils_IKEA _Sphere-Large | 1 | 1:19 | 45.38 | 15 | N | 0.2mm Layer Height, 0.4mm Nozzle Diameter | PLA
Adaptive_Utensils_IKEA _Sphere-Small | 1 | 0:42 | 20.85 | 15 | N | 0.2mm Layer Height, 0.4mm Nozzle Diameter | PLA
Adaptive_Utensils_IKEA _Straight-Large | 1 | 1:51 | 48.98 | 15 | N | 0.2mm Layer Height, 0.4mm Nozzle Diameter | PLA
Adaptive_Utensils_IKEA _Straight-Small | 1 | 1:42 | 25.15 | 15 | N | 0.2mm Layer Height, 0.4mm Nozzle Diameter | PLA

### Post-Processing

Use flush cutters (T02) to remove tree supports from the spoon and fork cores as well as the small and large finger support handles. Inspect the 3D printed parts for any printing defects, sharp edges, or burrs. Sharp edges and burrs can be removed with sanding or deburring tools.

## for IKEA IDENTITET

## MAKER GUIDE

Files available at https://github.com/makersmakingchange/Adaptive_Utensil_Handles_for_IKEA_IDENTITET | Page 7 of 15

### Examples of Quality Prints

Compare your 3D prints to the images here. If there are significant differences, you may need to reprint

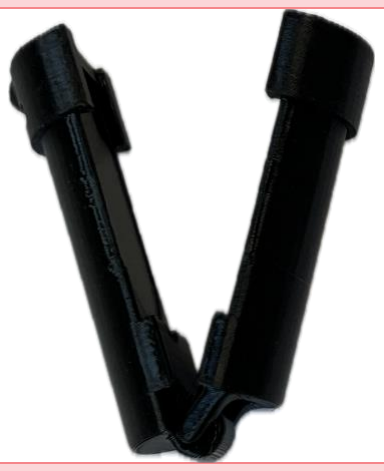
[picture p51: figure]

the part.

Adaptive Utensil Handles
Adaptive_Utensils_IKEA_Cor e-Fork

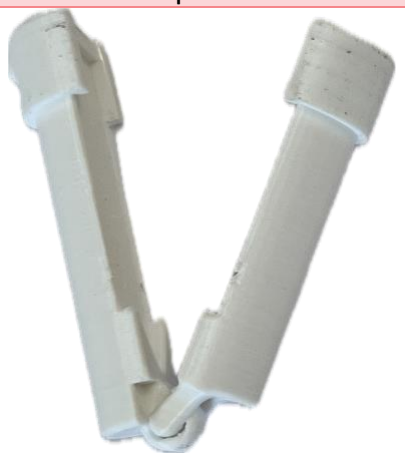
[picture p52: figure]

Adaptive_Utensils_IKEA_Core-Spoon

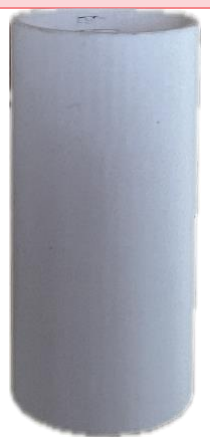
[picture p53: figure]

Adaptive_Utensils_IKEA_Shell

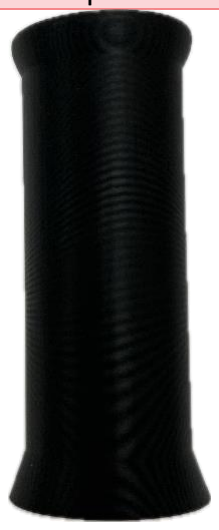
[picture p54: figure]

Adaptive_Utensils_IKEA_Elli pse

Adaptive_Utensils_IKEA_Finger Grip

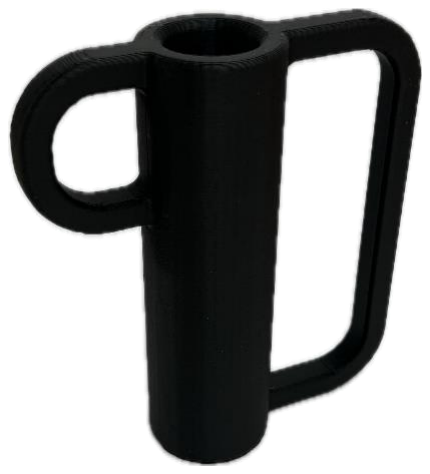
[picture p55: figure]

Adaptive_Utensils_IKEA_FingerSupp ort-Large

## for IKEA IDENTITET

## MAKER GUIDE

Files available at https://github.com/makersmakingchange/Adaptive_Utensil_Handles_for_IKEA_IDENTITET | Page 8 of 15

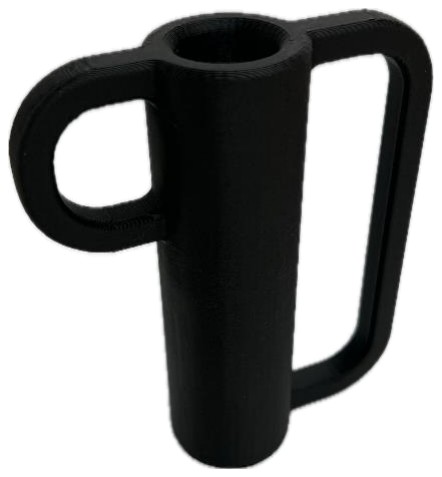
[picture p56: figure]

Adaptive Utensil Handles
Adaptive_Utensils_IKEA_FingerSu pport-Small

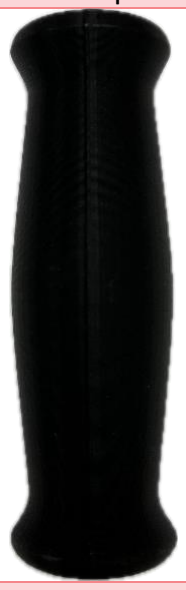
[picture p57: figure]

Adaptive_Utensils_IKEA_Rounde dGrip

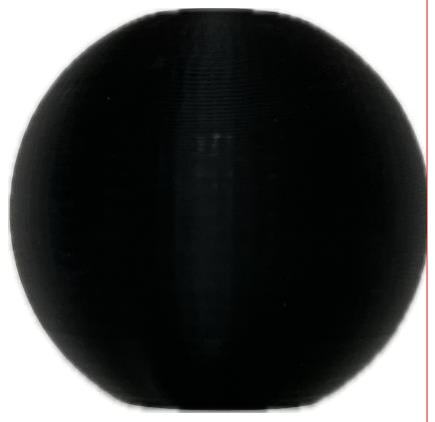
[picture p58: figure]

Adaptive_Utensils_IKEA_Sph ere-Large

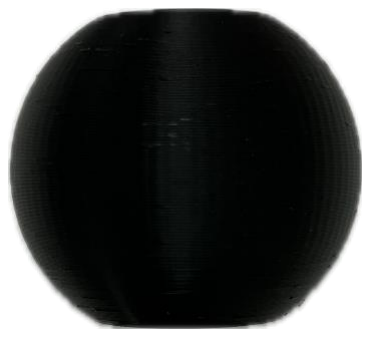
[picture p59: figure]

Adaptive_Utensils_IKEA_Sphere-Small

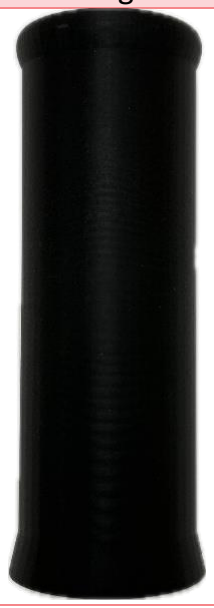
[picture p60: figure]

Adaptive_Utensils_IKEA_Straight -Large

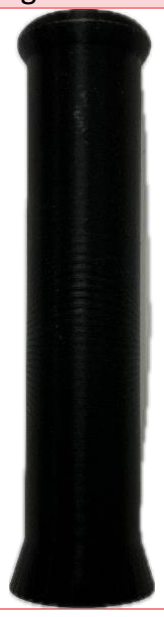
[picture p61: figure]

Adaptive_Utensils_IKEA_Stra ight-Small

## for IKEA IDENTITET

## MAKER GUIDE

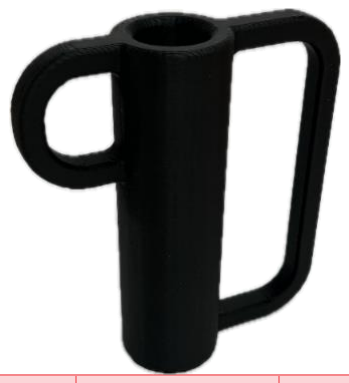
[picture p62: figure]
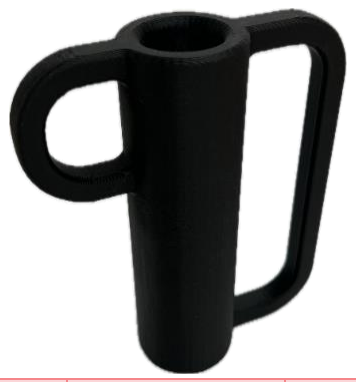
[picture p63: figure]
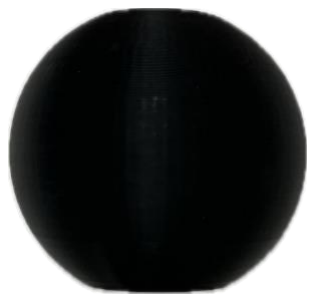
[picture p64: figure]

Files available at https://github.com/makersmakingchange/Adaptive_Utensil_Handles_for_IKEA_IDENTITET | Page 9 of 15

### Maker Component List

Adaptive Utensil Handles
A01 | Fork Core | QTY: 1 | A02 | Spoon Core | QTY: 1 | A03 | Shell | QTY: 2
A04 | Ellipse | QTY: 1 | A05 | Finger Grip | QTY: 1 | A06 | Finger Support- Large

QTY: 1

A07 | Finger
Support-Small
QTY: 1 | A08 | Rounded
Grip
QTY: 1 | A09 | Sphere-
Large

QTY: 1

A10 | Sphere-Small | QTY: 1 | A11 | Straight- Large
QTY: 1 | A12 | Straight-
Small

QTY: 1

## for IKEA IDENTITET

## MAKER GUIDE

Files available at https://github.com/makersmakingchange/Adaptive_Utensil_Handles_for_IKEA_IDENTITET | Page 10 of 15
A13 | IKEA
IDENTITET
FORK
QTY: 1 | A14 | IKEA IDENTITET SPOON

QTY: 1

## for IKEA IDENTITET

## MAKER GUIDE

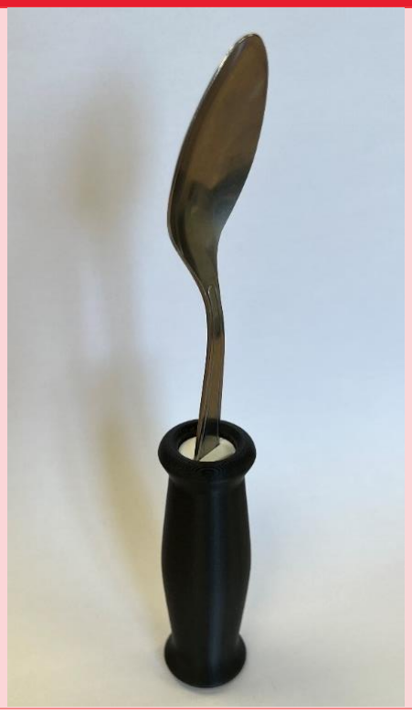
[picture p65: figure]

Files available at https://github.com/makersmakingchange/Adaptive_Utensil_Handles_for_IKEA_IDENTITET | Page 11 of 15

### Assembly Guide

Assembly Section
3D Printed Adaptive
Utensil Assembly

## for IKEA IDENTITET

## MAKER GUIDE

Files available at https://github.com/makersmakingchange/Adaptive_Utensil_Handles_for_IKEA_IDENTITET | Page 12 of 15

### Part A: 3D Printed Adaptive Utensils

Part A: Required Components
3D Printed Adaptive Utensils
A01 | Fork Core | QTY: 1 | A02 | Spoon Core | QTY: 1 | A03 | Shell | QTY: 2
A01 | Ellipse | QTY: 1 | A02 | Finger Grip | QTY: 1 | A03 | Finger Support- Large

QTY: 1

A01 | Finger
Support-Small
QTY: 1 | A02 | Rounded
Grip
QTY: 1 | A03 | Sphere-
Large

QTY: 1

A01 Sphere-Small

QTY: 1 | A02 | Straight-
Large
QTY: 1 | A03 | Straight-
Small

QTY: 1

## for IKEA IDENTITET

## MAKER GUIDE

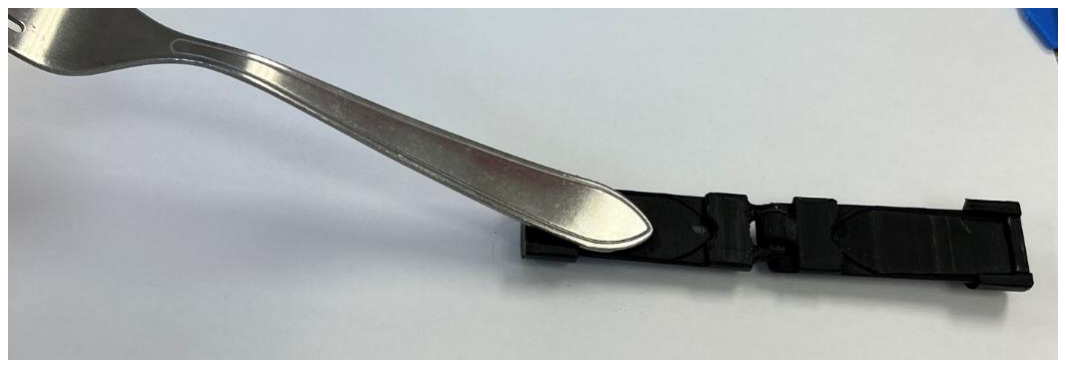
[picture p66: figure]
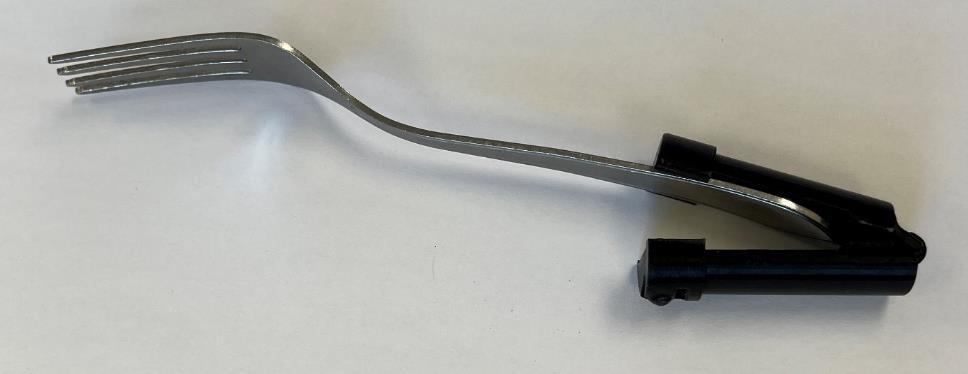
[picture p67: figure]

Files available at https://github.com/makersmakingchange/Adaptive_Utensil_Handles_for_IKEA_IDENTITET | Page 13 of 15

Part A: Required Tools and Supplies
- 3D Printer (T01)
- Scraper Tool (T02)
- Flush Cutters (T03)
- PLA Filament (S01)
- PETg Filament (S02)

Part A: Required Personal Protective Equipment (PPE)
- Safety Glasses (P01)

Part A: 3D Printed Adaptive Utensils Assembly Steps

Step A-01: Utensil Alignment
Press the utensil base into the profile cutout of the corresponding core.

Step A-02: Utensil Fit
Close the core halves around the utensil base.

## for IKEA IDENTITET

## MAKER GUIDE

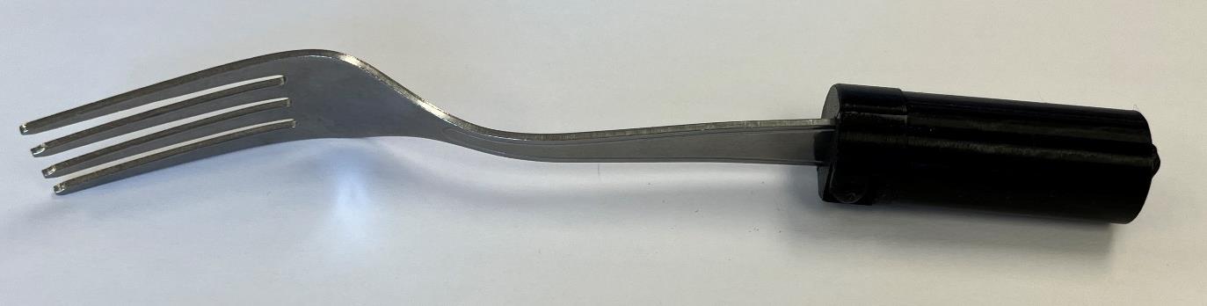
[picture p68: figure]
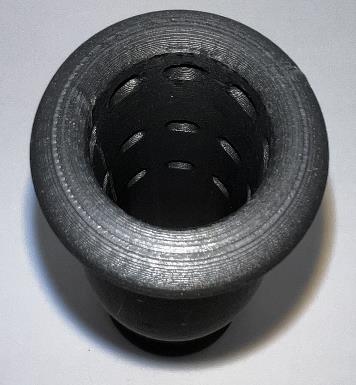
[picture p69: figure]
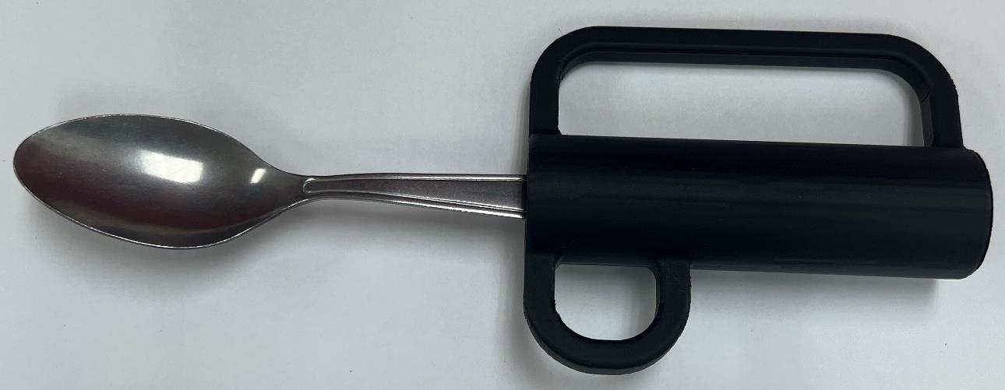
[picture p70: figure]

Files available at https://github.com/makersmakingchange/Adaptive_Utensil_Handles_for_IKEA_IDENTITET | Page 14 of 15

Step A-03: Core Assembly
Slide the shell around the core to lock it closed.

Step A-04: Handle Fit
Insert the core assembly into the 3D printed handle. Push and twist the utensil until the ball sockets press into the hemisphere cutouts inside the handle.

Step A-05: Adjustment
There are 3 levels of depth adjustment in increments of 20 mm and 8 levels of rotation adjustment in increments of 45° turns. To change depth and rotation, push, pull, and twist to lock the utensil in the desired position.

## for IKEA IDENTITET

## MAKER GUIDE

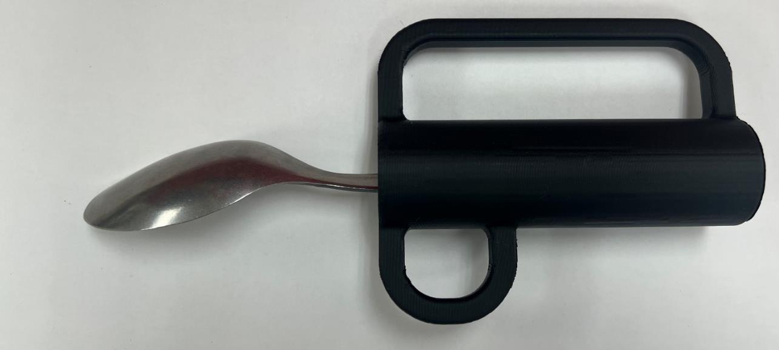
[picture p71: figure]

Files available at https://github.com/makersmakingchange/Adaptive_Utensil_Handles_for_IKEA_IDENTITET | Page 15 of 15

Assembly Complete

### Testing

Bend the cores open and closed for at least 3 cycles to break in/loosen the print-in-place hinges.

Once the core assembly is put together, test all depth and rotation configurations in each handle.

### Troubleshooting

If the core assembly does not lock inside the handle and slides during regular usage, that means the ball sockets did not properly align with the hemisphere cutouts. Continue to push, pull, and twist the core to find a locking position for the utensil. It may be easier to remove the core assembly, align the ball sockets, then insert the core straight into the handle.

The core assembly may become stuck inside a handle. First, try to pull out the core while rotating it with the utensil. If the core remains stuck, try pressing a thin and long object through the bottom hole of the handle to push it out.

When removing the core assembly, the shell may be left behind inside the handle. To remove the shell from the handle, use a finger or other thin and long object (like a pen) to dislodge it.

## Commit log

2025-04-16 Remove unused template files
    [Device_Name_BOM.csv, Device_Name_BOM.xlsx, OpenAT_Placard.f3d, OpenAT_Placard.stl]
2025-05-28 Add 3D Printing Files
    [IKEA_Core-Fork.STL, IKEA_Core-Spoon.STL, IKEA_Ellipse.STL, IKEA_FingerGrip.STL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]
2025-05-28 Add CAD files
    [IKEA_Core_Rev02.SLDPRT, IKEA_Ellipse_Rev02.SLDPRT, IKEA_FingerGrip_Rev02.SLDPRT, IKEA_FingerSupport-Large_Rev02.SLDPRT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]
2025-05-28 Add documentation
    [Adaptive_Utensils_BOM.csv, Adaptive_Utensils_BOM.xlsx]
2026-02-02 Rotated stls to match intended print orientation
    STLs were rotated to match the intended print orientation.
    [IKEA_Core-Fork.STL, IKEA_Core-Spoon.STL, IKEA_Ellipse.STL, IKEA_FingerGrip.STL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]
